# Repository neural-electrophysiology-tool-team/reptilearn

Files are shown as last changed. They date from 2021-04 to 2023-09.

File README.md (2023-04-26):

# Reptilearn

__ReptiLearn__ is an open-source software system for building automated behavioral arenas, running closed-loop experiments based on realtime video analysis, and collecting  behavioral data. 

__ReptiLearn__ was created to help us run continuous, long-term, learning experiments tailored to the specific needs and challenges posed by reptile model animals. 

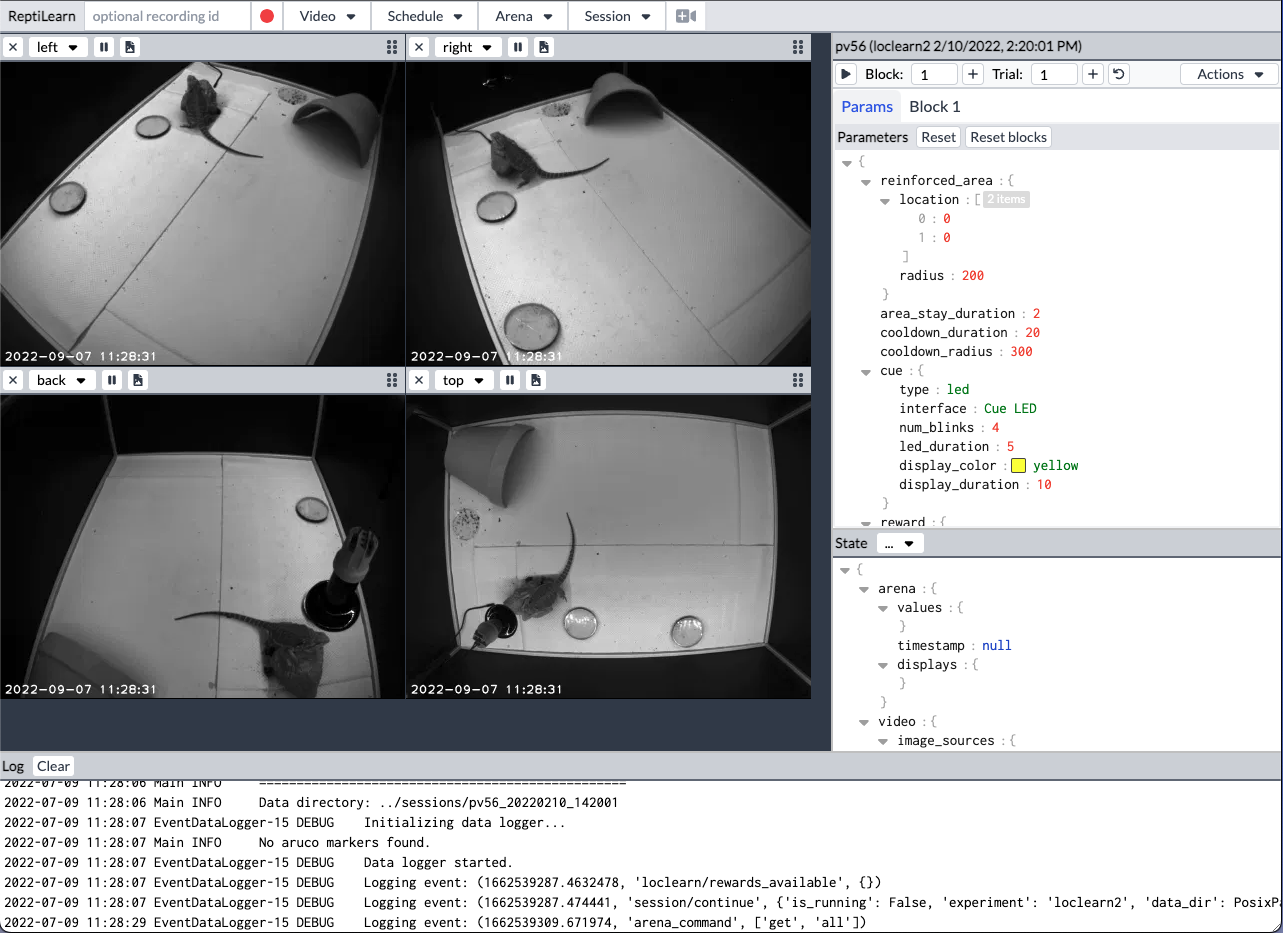
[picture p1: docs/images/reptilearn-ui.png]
ReptiLearn user interface


## Main Features

- Synchronized video recording and real-time analysis from multiple video sources
- Control of various arena hardware such as temperature sensors, lighting, and reward feeders
- Automate and run closed-loop behavioral experiments
- Web based interface for remote monitoring and control
- Highly extendable. Written purely in Python.

## Documentation

- [Getting started](docs/getting_started.md)
- [Building an arena](docs/build_arena.md)
- [Camera configuration](docs/camera_config.md)
- [Setting up the arena controller](docs/arena_setup.md)
- [Programming experiments](docs/programming_experiments.md)
- [Extending the video system](docs/programming_video_system.md)
- [Scheduling tasks](docs/adding_tasks.md)

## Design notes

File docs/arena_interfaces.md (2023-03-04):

# Interface documentation

This document describes the available arena controller interface types and their configuration parameters. 
See [Setting up the arena controller](arena_setup.md) for more information.

## Common interface attributes

- name: Interface name for identification. NOTE: Interface names should be unique across all connected boards.
- type: The interface type. Currently one of `line trigger feeder dallas_temperature`. Each one is explained below.
- ui: Determines how this interface is controlled in the ReptiLearn user interface.

## Interface types and attributes
There are a number of supported interfaces. The `"type"` attribute determines which one is used.

### `line`
Control a single digital output pin. Useful for turning things on and off.

Attributes:
- `pin`: Integer. The Arduino digital pin number to use.
- `reverse`: true | false. Reverse the line output. Will output HIGH when its  state is 0 and LOW when it is 1. 

Commands:
- `get`: Sends back the current state of the line - 0 or 1.
- `toggle`: Set the line state to the opposite of the current one.
- `set <x>`: Set the line state to <x> (0 or 1)
- `periodic <0|1> <period_dur>`: Control toggling the line on and off at a fixed rate. For example `periodic 1 500` will start toggling every 500 ms. `periodic 0` will stop the toggling. The period can be reliably timed at quite short durations. This is useful for blinking LEDs, etc.

Example:
```json
{
    "name": "LED",
    "type": "line",
    "pin": 12,
    "ui": "toggle"
},
```

### `trigger`
Output pulses at a fixed frequency on a single pin. This is used for synchronizing frame acquistion of multiple cameras.

Attributes:
- `pin`: Integer. The Arduino digital pin number to use.
- `pulse_len`: Integer. Time duration in milliseconds between successive pulses. For example, to acquire frames at 20 frames per second this attribute should be 50.
- `pulse_width`: Float. A number between 0 and 1. The pulse duty cycle. The fraction of the pulse period in which the output will be on. For example, a value of 0.8 with a pulse_len of 50ms will result in the digital pin going HIGH for 40ms and then LOW for 10ms before going HIGH again.

Commands:
Like the `line` interface, the `trigger` interface inherits from the toggle interface and has the same commands (`get`, `set`, `toggle`, `periodic`). See the line interface documentation.

Example:
```json
{
    "name": "Camera Trigger",
    "type": "trigger",
    "pin": 12,
    "pulse_len": 17,
    "pulse_width": 0.7,
    "ui": "camera_trigger"
}
```

### `feeder`
Control an EVNICE EV200GW fish feeder (or similar)

Attributes:
- `pins`: Array of 4 integers. The numbers of the pins that are connected to the ULN2003 board.

Commands:
- `dispense`: Dispense one reward from the feeder.

Example:
```json
{
    "name": "Right Feeder",
    "type": "feeder",
    "pins": [5, 6, 7, 8],
    "ui": "action",
    "command": "dispense",
    "icon": "gift"
}
```

### `dallas_temperature`
Communicate with digital temperature sensors such as DS18B20 (one-wire protocol). This uses the DallasTemperature arduino library. Check the [library documentation](https://github.com/milesburton/Arduino-Temperature-Control-Library) for supported devices. This interface can control any number of such sensors connected in parallel over a single Arduino digital pin.

Attributes:
- `pin`: Integer. The one-wire digital pin number. 

Commands:
- `get`: Sends back an array of floats containing the current measurement of each sensor.

Example:
```json
{
    "name": "Temp",
    "type": "dallas_temperature",
    "pin": 2,
    "ui": "sensor",
    "unit": "°",
    "icon": "thermometer-half"
}
```

## Interface UIs
The `ui` attribute determines how the interface is presented in the Arena menu of the ReptiLearn UI. Each `ui` type can have additional interface attributes that configure how it will be displayed in the menu.

### `toggle`

A toggle button that allows setting the interface on or off. It has no additional attributes.

Compatible interfaces: `line`

### `trigger`
This `ui` value tells ReptiLearn to use this interface as a camera trigger. The trigger can be controlled from the trigger button next to the recording button in the UI, or automatically when starting and stopping video recording (in case the trigger was not already running before recording). There are no additional attributes.

Only one interface with the `trigger` ui is supported. Additional interfaces will be ignored by the recording system.

Compatible interfaces: `trigger`

### `action`

A button that sends a command without arguments to the interface. This can be any command.

Attributes:
- `command`: String. The command name. For example, for controlling a `feeder` interface manually it should be set to `dispense`.
- `icon`: String. A name of a FontAwesome icon that will be displayed on the button. See [here](https://fontawesome.com/search?o=r&m=free) for available icons.

Compatible interfaces: any interface that has commands without arguments (e.g. `feeder`)

### `sensor`

Displays the sensor reading, possibly listing multiple sensors that send on the same interface (as in the `dallas_temperature` interface).

Attributes:
- `unit`: String. The units of the sensor value.
- `icon`: String. A name of a FontAwesome icon that will be displayed on the button. See [here](https://fontawesome.com/search?o=r&m=free) for available icons.

Compatible interfaces: `dallas temperature` (but can be used to display the value of any interface).

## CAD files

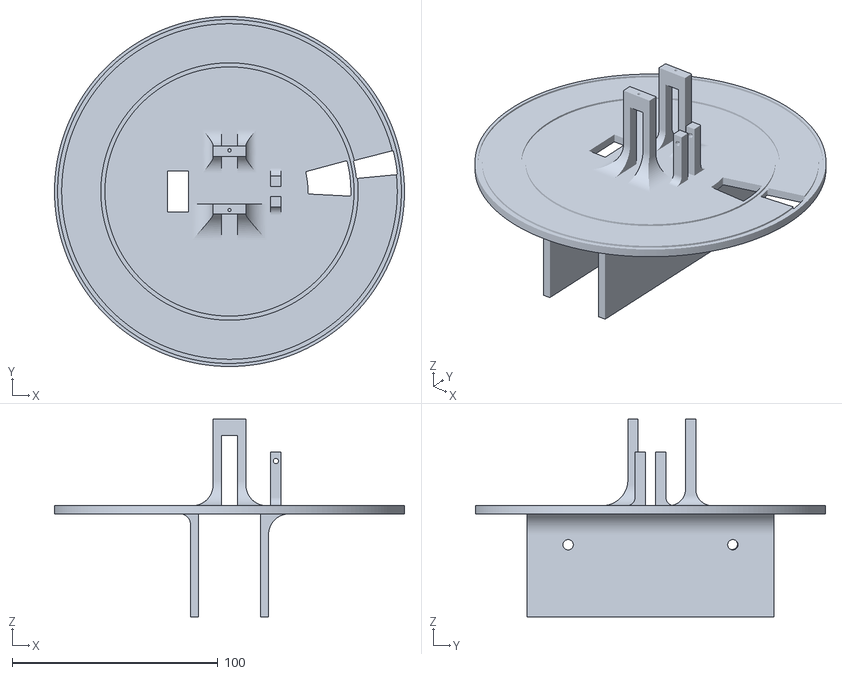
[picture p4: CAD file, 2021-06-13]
autofeeder_project/Base.stl
170.0 x 170.0 x 96.0

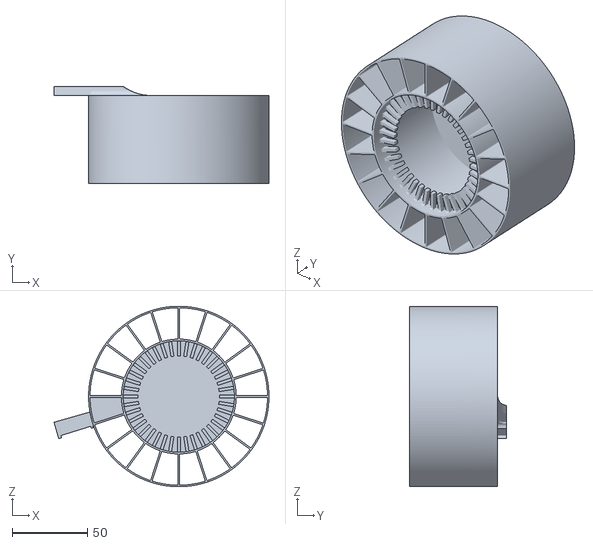
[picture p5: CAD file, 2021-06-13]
autofeeder_project/first_cyn.stl
143.0 x 64.7 x 120.0

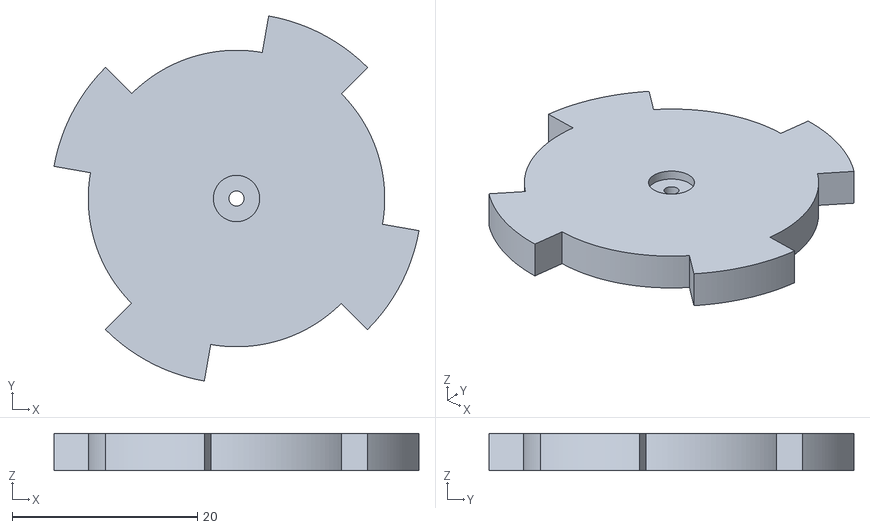
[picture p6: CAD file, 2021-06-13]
autofeeder_project/myGear.stl
39.4 x 39.4 x 4.00

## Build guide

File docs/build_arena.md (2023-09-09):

# How to build a ReptiLearn Arena

This document describes how we built our automated arenas for studying various reptiles. We take no responsibility for any damage caused as a result of following this guide.

## Arena

First build the Arena container.

1. Obtain and cut the wall sheets and frame as necessary (explained elsewhere).
2. Stick anti-reflection wallpapers on the walls. We used black self-adhesive wallpaper rolls suitable to be used as a chalkboard. 
3. Build a box. We used aluminum profiles for the frame and Alucobond sheets for the walls and floor. The floor size was 100x70 cm, and the walls height was 45cm. 
4. To support the top-view camera and other devices (e.g. heat lamps), add another profile one meter above the floor, spanning along the long axis of the box. The profile can be supported by two more profiles connected to the short sides of the box.
5. Connect adjustable camera arms to the top frame of the box, and optionally an additional one on the profile you added on the previous step. We used [this product](https://www.noga.com/Products/modu/Modular%20Holders/LC6100/LC_Arms_-_LC6100). To connect the cameras we used a 3d-printed camera holder that connects the arms to the cameras with screws (STL file TBD).

## Electronics

`General soldering advice: Prevent short-circuits! Use heat shrink tubes for insulation and don't leave any uncovered wires.`

* Decide where and how to place your electronics. This determines the length of the cables you will need to make. Some box or a plate to hold the components could be useful.
* Electronic devices are controlled using Arduino boards. We use “Arduino Nano Every” boards. They are quite inexpensive, have a large enough memory to fit our program, and can be easily mounted on a prototyping breadboard. Other Arduino boards could be used as well but might have a different pinout and/or memory size. Some Arduino boards use 3V instead of 5V. _We didn’t test 3V boards, and some of the components described below might not work in 3V._

### Part 1: Synchronized Camera Trigger (Arduino 1 / 2)

When recording from multiple cameras it’s often desirable that all cameras expose their sensors and take images at the same time. There are several schemes for doing that. We use a single source to trigger all the cameras. One Arduino board is programmed (see elsewhere) to send TTL pulses on one of its output pins. This pin is connected in parallel to the GPIO input of each camera. A two strand cable should go from the Arduino output pin and ground pin (gnd) to the camera GPIO input and ground. Consult the camera manual for the specifics of using its GPIO inputs. In the case of **FLIR cameras** we use their GPIO cable that connects to the camera on one side and has colored wires on the other. ReptiLearn sets the cameras to use Line3 by default (but this can be changed). For example, for a Firefly camera, this page: [Input/Output Control FFY-U3-16S2](http://softwareservices.flir.com/FFY-U3-16S2/latest/40-Installation/InputOutputControl.htm) will tell you to connect the Arduino output to the green wire and the ground pin to the brown wire.

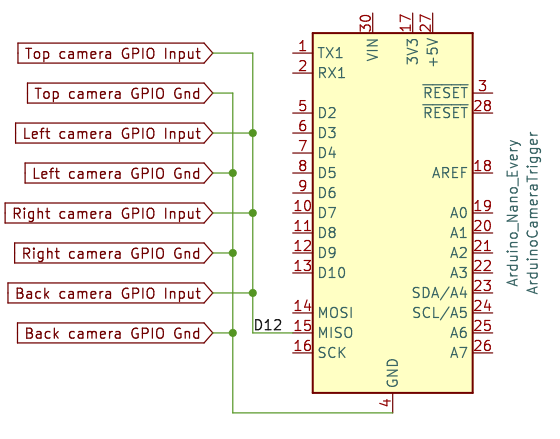
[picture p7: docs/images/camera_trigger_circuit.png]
Camera trigger circuit diagram


Connection diagram showing how to connect four cameras to an Arduino Nano Every board. To find the location of each I/O connection on the board check this page (for this specific board): [Nano Every | Arduino Documentation](https://docs.arduino.cc/hardware/nano-every). Look for the pinout.

```
Note: Don't use the camera trigger Arduino board for anything other than sending triggers. Communication with other components might cause the trigger timing to vary.
```

### Part 2: The Feeder (Arduino 2 / 2)

To reward the animals we used a Fish Feeder (EVNICE EV200GW). This feeder normally has a latency of about 15 seconds which might not be acceptable for some tasks. We reduced the latency to about 3 seconds by interfacing directly with the feeder motor. 

The feeder has a 28BYJ-48 stepper motor. We control it by connecting it to a ULN2003 stepper motor driver board that looks like this:

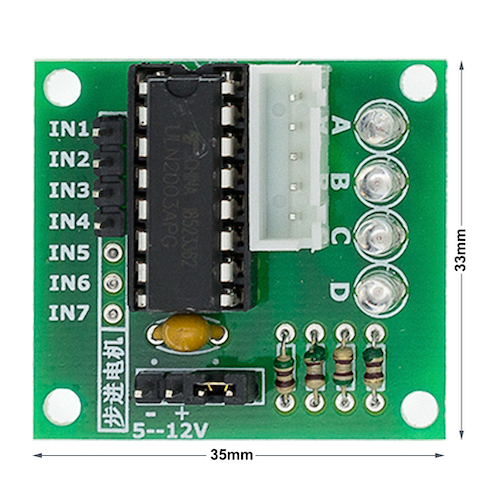
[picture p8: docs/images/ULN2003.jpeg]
ULN2003 Board


The layout of this specific board is easy to work with as you’ll see. As mentioned, you shouldn’t connect this to the camera trigger Arduino. Use a second one and follow these steps:

1. Unscrew and remove the bottom plastic cover of the feeder
2. Remove the plastic cover that hides the motor
3. Disconnect the motor cable from the feeder board and connect it to the white header on the ULN2003 board.
4. The feeder has a DC power socket. This socket is connected to the board with a small cable with 2 wires. Disconnect it from the board and connect it to the power inputs on the ULN2003 board (usually marked + -, black header on the right side in the picture above). The red power wire goes to the +, the black goes to the minus (ground). To make this connection we use male to female dupont jumper wires. The male pins can be inserted into the correct pins of the 3-pin socket, and the female pins connect to the ULN2003 board. Alternatively you can cut off the 3-pin socket and solder dupont female pins directly to the black and red wires. Technically the ground should also be connected to the Arduino GND pin but we found this to be usually unnecessary. This is the first thing to check if something doesn’t work, though.
5. Connect the four inputs marked IN1-IN4 to digital pins on the Arduino board (e.g. D9, D10, D11, D12).
6. Close and screw the bottom cover back, making sure all the wires can get to where they need to be. There are 4 LEDs on the board that light up in sequence during feeding, you might want to hide or show these depending on your needs.
7. Use the mounting mechanism provided together with the feeder to fix everything to the top frame of the arena.
8. Connect a 5V DC power supply to the DC power socket on the feeder. A maximum current of about 500mA should be enough.

Our setup is very similar to the one described [here](https://lastminuteengineers.com/28byj48-stepper-motor-arduino-tutorial/)

### Part 3: Temperature sensors

We use two digital DS18B20 temperature sensors for measuring temperature conditions in the arena. These can come in a metal or plastic packaging and have 3 wires. They use the [1-Wire](https://en.wikipedia.org/wiki/1-Wire) protocol to communicate with the Arduino, enabling up to 128 sensors to be connected in parallel using a single Arduino digital pin.

See [here](https://lastminuteengineers.com/multiple-ds18b20-arduino-tutorial/) for more info.

* The sensor has 3 IO pins: VDD (5v), GND (ground), and DQ. First figure out which wire is which.
* Then, for each sensor, use a cable with 3 or more wires, and connect VDD to the +5V pin of the Arduino board, GND to the GND pin, and DQ to a digital I/O pin. 
* Additionally, VDD and DQ must be connected with a 4.7kOhm pull-up resistor. The resistor can be shared between all sensors (each DQ to one side of the resistor and each VDD to the other).

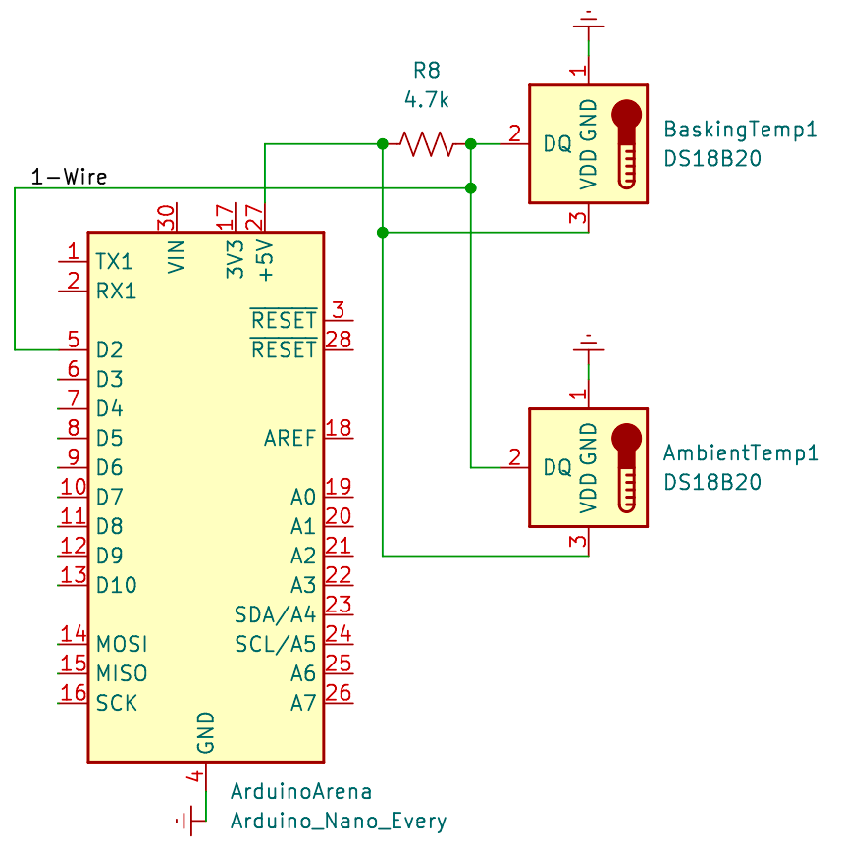
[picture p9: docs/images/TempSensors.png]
Temperature Sensors circuit diagram


### Part 4: Controlling things with relays

A relay is a mechanical device that can close or open a circuit based on a control voltage. Any device that requires a high current, which you want to switch on and off requires a relay. We used relays for controlling an LED strip that lights the arena, as well as heat lamps.

We used [this](https://www.pololu.com/product/2480/) board which includes an Omron G5LE-14-DC5 SPDT relay.

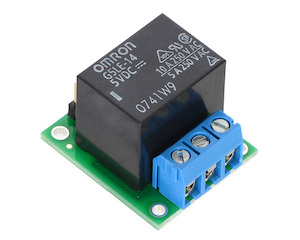
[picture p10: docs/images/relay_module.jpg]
Relay module


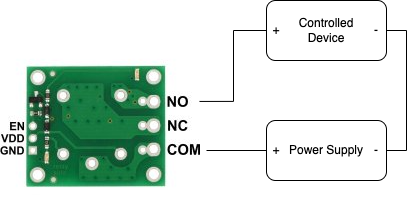
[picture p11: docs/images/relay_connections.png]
Example relay circuit diagram


The relay board has 6 I/O connections. EN, VDD, and GND connect to the Arduino board (male pins in front of the image above), and NO, NC, and COM are the controlled connections (blue socket with screws in the back of the image above). Connect VDD to the Arduino +5V pin, and GND to the Arduino GND (ground) pin. EN, the signal pin, should be connected to one of the Arduino’s digital output pins. 

The relay has two modes of operation depending on which connections are used for connecting the controlled device. The NO (Normally open) pin is connected to the COM (common) pin only when the EN pin is high (i.e., when there’s a 5v voltage between EN and GND). The NC (Normally closed) pin is connected to the COM pin only when the EN pin is low (no voltage across EN and GND). We always use the NO pin so that current will only arrive to the device when the Arduino is running and its digital pin is high.

In practical terms one of the wires going from the power supply to the controlled device (positive in the diagram above) should be cut somewhere in the middle, and then the half that goes from the power supply should be connected to COM, and the other half to NO (see diagram above).

We connected both a LED strip and heat lamps using this method. The relay can be connected to either the AC or DC part of a DC power supply. You may want to connect multiple devices to the same power supply in parallel (e.g. multiple heat lamps to the same power supply). In this case you would want to connect the relay to each cable that connects the power supply to one of the devices in order to be able to control each device individually.

### LED Strip

We used a 12V cold-white LED strip to light the arena. The LED strip is taped to the top frame and covers the four top edges of the arena. This results in a mostly uniform light level across the arena floor, and helps to minimize shadows. The total length is then around 3.4 meters, which required a 12V 5A DC power supply for the strips we used (consult your LED strip manufacturer for the maximum current it might draw, and adjust the power supply as necessary).

### Heat Lamps

We had success using these [IR halogen heat lamps](https://he.aliexpress.com/item/4001212438174.html?spm=a2g0o.productlist.0.0.3b561783JmP4VQ&algo_pvid=f1c2b25b-032a-41a0-b267-9318c73811c5&algo_exp_id=f1c2b25b-032a-41a0-b267-9318c73811c5-25&pdp_ext_f=%7B%22sku_id%22%3A%2210000015319775871%22%7D&gatewayAdapt=glo2isr).

They are 24V 50W DC lamps which means that they will need a current of at least 50/24=~2A per lamp, however halogen lamps can have a much lower resistance when they are cold and therefore can take much more current initially. It is recommended to use a power supply with at least double the current (e.g. 4A per lamp or more). We used a 24V 12A DC power supply for two lamps.

## Touch screen

A touch screen can be connected to the arena computer in the usual way. ReptiLearn has support for switching the screen on or off (linux only, currently). 

We used a Dell monitor with good results for behavioral experiments. For using a touch screen while making electrophysiological recordings, we used [this monitor](https://www.connection.com/product/elo-touch-solutions-accutouch-1790l-17-lcd-open-frame-touchscreen-display-hdmi-vga-displayport-usb/e326347/34520493?cac=Result) to reduce electromagnetic noise.

We mount the monitor using screws to one of the shorter (0.7m) sides of the arena. A Kappa board or some other strong board can be used to hide the monitor cables and prevent the animal from using the monitor to escape. Cut it to fit into the arena, and make a square hole that fits the monitor (that is, make a frame for the monitor).

## Finishing touches

Once everything is built, follow these final steps:

* Mount the cameras using the camera holders
* Connect Cameras and Arduino boards to the computer using USB cables. Make sure the camera cables support a fast enough USB mode to reach the frame rates you want to record in. We had success with the [FLIR USB cables](https://www.flir.eu/products/usb-3.1-locking-cable/) that are sold on their website.
* Connect GPIO cables to cameras
* Place Arduino boards and other electronic components in their final location (e.g. a box or plate)
* Hide cables and make it look tidy and neat.
* Connect power supplies
* [Setup the ReptiLearn software](getting_started.md)
* Have fun

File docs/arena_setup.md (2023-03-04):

# Setting up the arena controller

ReptiLearn can control and monitor various electronic devices by communicating with [Arduino boards](https://www.arduino.cc/). Some examples include lights, cue LEDs, temperature sensors, reward feeders, and camera triggers. 

You can connect any number of devices to one or multiple Arduino boards, and control all of them without having to write any Arduino code. This is accomplished by using a single Arduino program that can interface with a number of different types of components. Each Arduino board is automatically programmed with the same generic program, and once communication between the board and computer software is established, each board is configured based on its individual settings.

## The arena controller

Communication with, and programming of the boards is handled by the Arena controller ([arena.py](../arena/arena.py)). The ReptiLearn software communicates with the controller using the [MQTT](https://mqtt.org/) protocol. The controller provides bi-directional communication between MQTT clients and connected Arduino boards.

By default, ReptiLearn will start the arena controller as a sub-process when it starts up, unless the arena config file is empty. It's also possible to run the controller separately, or even on a different computer. See [here](#run-arena-controller-separately) for more information. In the rest of the document it's assumed you're running the controller as a sub-process.

## Supported Arduino boards

The arena controller should work with any Arduino board that has at least 48KB of program memory and 4KB of RAM. Check your model specifications. At the time of writing, most available boards do not have enough memory. We used Arduino Nano Every boards which work well and are relatively low cost.

## Configuring the arena controller

The arena config file is stored by default in `reptilearn/system/config/arena_config.json`. To make changes you can use the arena settings dialog:

- Run ReptiLearn
- Open the ReptiLearn web app in a browser
- Open the Arena menu by clicking the button
- Click on "Arena settings" to open the settings dialog

### Adding Arduino boards

- Connect an Arduino board
- In the settings dialog, click the plus (+) button
- You should be able to select the port of the board in the dialog that opens.
- Choose a name for this Arduino, and fill in the FQBN of your board (see below).
- Click the add button
- The new board configuration should appear. 
- Click on the save button to save the new config file.

### Fully qualified board name (FQBN)

The FQBN string identifies the Arduino board type, and is necessary for uploading programs to the Arduino. To find the FQBN of your board run:

```bash
arduino-cli board listall
```

For example for __Arduio Nano Every__ the FQBN is `arduino:megaavr:nona4809`.

### Uploading the program

After you saved the arena configuration you can upload the program to the Arduino board you added:

- Open the "Arena settings" again
- Choose the new board from the board list (according to the name you chose when you added it)
- Click on "Upload program"

The upload process should begin and you should see messages in the log.

### Not enough memory error
As mentioned above, many Arduino boards do not have enough memory to store the arena program and run it. If you use one of these boards you will encounter a "not enough memory" error while trying to upload.

In most cases getting a supported board model should solve this problem, however it's also possible to reduce the storage space requirements of the program by removing unnecessary interface types from the source code. To do that, open [arena/arduino_arena/arduino_arena.ino](../arena/arduino_arena/arduino_arena.ino), and comment out any of the lines that start with `#include` for interfaces that you don't need. See the comment in the includes section of the .ino file.

### Connecting multiple boards

You can repeat the previous steps with any number of additional Arduino boards. It is recommended to connect the boards one-by-one, to make them easier to identify.

### Adding interfaces

After adding an arduino board you need to configure its interfaces. These define which devices are connected to the board and their parameters, including how they will appear in the Arena menu. 

You can configure interfaces in the "Arena settings" dialog. After choosing the Arduino board you want to configure, the interfaces array should show up in the configuration editor. As a simple example, edit your config to look like this:

```json
{
    "serial_number": "<board serial>",
    "fqbn": "<board fqbn>",
    "interfaces": [
        {
            "name": "LED",
            "pin": 13,
            "type": "line",
            "ui": "toggle"
        }
    ]
}
```

Then click the save button, and if the arena controller wasn't already running, open the Arena menu and click "Start arena".

Assuming all went well, the controller should now run and the new interface should appear in the Arena menu. Clicking on the interface button (labeled LED with a toggle icon) should turn on the LED.

See [here](arena_interfaces.md) For more information about interfaces.

NOTE: Some boards have a built-in LED connected to pin 13. If that's not the case for your board, you can connect one between pin 13 and the ground pin of the board (if needed use an appropriate resistor in serial with the LED). 

### Allow get

The system periodically polls each board for its current state (every minute by default). It also requests the value of each interface after sending it a command. This might take some time and prevent the board from doing other things, therefore it should be avoided for time-sensitive functions (such as the camera trigger).

The `allow_get` board parameter can be set to `false` in the arena config in order to prevent sending these state updates. 

## Arena menu

The Arena menu in the web app lets you manually send commands and monitor sensors, as well as stop and re/start the arena controller. Each interface is displayed in the menu according to its configuration. The "Poll arena" button will request each board for its current state and update the menu and system state accordingly.

## Run the arena controller separately

The arena controller can be run as a separate program instead of as a sub-process of the main system. This allows running the controller on a different computer. In this case it's not possible to program the boards or start and stop the controller from the ReptiLearn web app.

To run the controller on another computer, download and install reptilearn as described [here](getting_started.md#installation) on both computers. Make sure to install [Arduino-CLI](getting_started.md#arduino-cli-optional) on the computer that will run the arena controller.

To prevent ReptiLearn from running the controller on startup open your config file and set the `run_controller` attribute in the arena dictionary to False. For example:

```python
arena = {
    "run_controller": False,
}
```

Restart ReptiLearn if it's already running for the change to have effect.

### Configuration

Here we assume you are running the controller from the same ReptiLearn installation as the ReptiLearn system. See more information [below](#running-remotely) if you want to  run it remotely.

#### Adding boards

When running the controller separately it's not possible to find available boards in the "Add Arduino" dialog, as before. To find the serial number of your arduino, open a terminal pointing to the reptilearn directory (use Anaconda prompt on windows), and run the controller with the `--list-ports` argument:

```bash
cd arena
conda activate reptilearn
python arena.py --list-ports
```

You should see a list of all available serial ports with their serial numbers. Find the FQBN of your board with `arduino-cli` as explained [above](#fully-qualified-board-name-fqbn).

### Uploading the program

After configuring the boards in "Arena settings", use the controller again to upload the program. Upload to all configured boards by running:

```bash
cd arena
conda activate reptilearn
python arena.py --upload
```

To upload to a specific board run:

```bash
python arena.py --upload <board_name>
```

Where <board_name> is the name that was chosen when configuring the board.

### Running the controller

To run the controller open a terminal (Anaconda prompt in Windows) window pointing to the reptilearn directory, and run:

```bash
cd arena
conda activate reptilearn
python arena.py
```

OR if you want to use a different config module than the default (the default is at arena/config.py):

```bash
conda activate reptilearn
cd arena
python arena.py --config config-module
```

where `config-module` is the name of a python module containing the config values without the .py extension.

Once the board is running, log messages should appear in the ReptiLearn web app, and the Arena menu should show the configured interfaces.

Press Ctrl-C to stop the controller.

### Running remotely

When running the controller on a different computer its necessary to set the same MQTT broker host and port, in both the ReptiLearn config file, and the controller config file at [arena/config.py](arena/config.py). See [here](getting_started.md#remote-mqtt-broker) for more information on using a remote MQTT broker.

Both installations should also have a copy of your `arena_config.json` file. This is the file that is edited using the "Arena settings" dialog. You can usually find it at `system/config/arena_config.json`, but you can change its location by editing `arena_config_path` in both config files.

After doing the previous steps, you can run both ReptiLearn and the arena controller as described above. They should be able to communicate with each other through the MQTT broker.

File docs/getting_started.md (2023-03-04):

# Getting started

## Installation

The software was mostly tested on Ubuntu 20.04, but also works on MacOS, Windows, and probably other linux distributions (although some features might not work).

Follow these steps to install:

### Download

- Install [Git](https://git-scm.com/downloads)

- Open a terminal (git bash on windows), change the directory to where you want to install, and run:
 
 ```bash
 git clone https://github.com/neural-electrophysiology-tool-team/reptilearn
 ```

### Setup Python environment

- Install [Anaconda](https://www.anaconda.com/)

- Run the following from the same directory to create a reptilearn Python environment (on Windows use Anaconda Prompt):

```bash
cd reptilearn
conda env create -f environment.yaml
```

This should install all the necessary Python dependencies.

### Build the UI webapp

- Install [Node.js](https://nodejs.org/en/)

- Run the following in a terminal window pointing to the `reptilearn` directory to install node.js dependencies and build the webapp:

```bash
cd ui
npm install
npm run build
cd ..
```

### MQTT broker (optional)

Communication with Arena hardware and other software components (e.g. touchscreen apps) is done using the [MQTT](https://mqtt.org/) protocol. When starting up ReptiLearn it tries to connect to an MQTT broker running on the same machine on the default MQTT port (1883). If a connection was not successful you will see an error message, but other parts of the system can still be used.

We recommend installing [Eclipse Mosquitto](https://mosquitto.org/). To use a broker running on a different machine see [Remote MQTT broker](#remote-mqtt-broker) below for more information.

NOTE: ReptiLearn doesn't currently support non-anonymous access to the MQTT broker. If you're using Eclipse Mosquitto and have problem connecting (connection refused), add the following line to your mosquitto.conf file:

```
allow_anonymous true
```

### Arduino-CLI (optional)

For programming Arduino boards you need to install [arduino-cli](https://arduino.github.io/arduino-cli/latest/installation/).

Once installed, run these commands to install the necessary Arduino libraries:
```
arduino-cli core update-index
arduino-cli lib install AccelStepper ArduinoJson OneWire DallasTemperature
```

Finally, install the software for your specific Arduino board model(s). For example for an Arduino Nano Every or UNO WiFi Rev 2 run:
```
arduino-cli core install arduino:megaavr
```

For other models, the following command will list all available board IDs:
```
arduino-cli core list --all 
```

When you have your board ID, install the core for it using this command:
```
arduino-cli core install <board ID>
```

Repeat this for each type of board you intend to use.

### FFmpeg setup (optional)

[FFmpeg](https://ffmpeg.org/) is used to encode video files. Normally it should be installed together with the ImageIO library when creating the anaconda environment, however if you want to use a different installed version (for example one that supports encoding on a GPU), create the file `reptilearn/system/.env` with the following content:

```
IMAGEIO_FFMPEG_EXE=/path/to/ffmpeg/executable
```

## Configuration

The system uses python modules as configuration files. The default configuration can be found at [system/config/config.py](/system/config/config.py). You would probably want to make some changes before running for the first time. It's possible to make changes directly in the default config file, but we recommend creating a new config file (e.g. system/config/my_config.py). 

Any values not defined in the new config file will be taken from the default config file. To use the new config, run with a `--config my_config` command line argument (see [Running](#running) below).

For example, this is how a config file that only changes the web server port value would look like:
```python
web_ui = {
    "port": 3501,
}
```

You probably want to change the directories for storing data:

- `session_data_root`: This is where session data will be stored (each session is stored in its own subdirectory)
- `media_dir`: Videos and images are stored here when there's no open session

Make sure these directories exist before running.

## Running

- If you're using a local MQTT broker, make sure it's running
- In a terminal (Anaconda Prompt on Windows) switch to the installation directory and run:

```
cd system
conda activate reptilearn
python main.py
```

OR if you want to use a different config module:

```
cd system
conda activate reptilearn
python main.py --config my_config
```

where `my_config` is the name of a python module inside the `config` directory without the .py extension.
For example, ```python main.py --config config2``` will start the system configured according to `system/config/config2.py`.

- Open a recent version of your favorite web browser, and go to [`http://localhost:3500`](http://localhost:3500). You can access the web app remotely by using an ssh tunnel or by using the computer's IP address instead of `localhost`.

NOTE: We recommend using ssh tunnels and/or a VPN to securely access the web app. ReptiLearn has no support for user authentication or any other security measures.

## Database

A [TimescaleDB](https://www.timescale.com/) database can optionally be used to store log data. To use this feature, you first need to install the database (see the link above for information). [Docker image installation](https://docs.timescale.com/install/latest/installation-docker/) is recommended. 

If you use the Docker image, you must also install [`psql`](https://www.timescale.com/blog/how-to-install-psql-on-mac-ubuntu-debian-windows/) separately.

Once `psql` is installed, install the [psycopg2](https://pypi.org/project/psycopg2/) library into the anaconda environment you created previously:

```bash
conda activate reptilearn
pip install psycopg2
```

Lastly, you need to create a new database. This can be done by running the SQL command (this can be done using [psql](https://www.postgresql.org/docs/current/app-psql.html)): 
```sql 
CREATE DATABASE reptilearn;
```

## Real-time object detection using YOLOv4

ReptiLearn currently supports real-time object detection using the YOLOv4 neural network model. YOLO can be used to obtain bounding boxes of relevant objects in image streams (such as your subject animals). We use the original darknet version from [this](https://github.com/AlexeyAB/darknet) repository. Darknet requires a CUDA capable GPU, and working installations of NVIDIA CUDA, and cuDNN.

First, configure your cameras or other image sources (see [Camera configuration](docs/camera_config.md) for more information), then follow these steps to setup the model:

- [Compile darknet](https://github.com/AlexeyAB/darknet#how-to-compile-on-linux-using-make). We recommend using the `make` method. Make sure to set `LIBSO=1` in the `Makefile` to compile into a static library.

- Copy the compiled library `libdarknet.so` from the YOLOv4 directory into `reptilearn/system/image_observers/YOLOv4`

- Generate/copy model weights and configuration: To train the model to detect your custom objects follow this [section](https://github.com/AlexeyAB/darknet#how-to-train-to-detect-your-custom-objects) in the darknet documentation. Another option is to use pre-trained weights. In either case you should end up with three files: A `.cfg` file containing your network configuration, an `obj.names` file containing a list of object classes, and a `.weight` file containing the trained model weights. Copy these files into `reptilearn/system/image_observers/YOLOv4`.

- Add the YOLOv4 image observer: In the ReptiLearn web app, open the `Video` menu and click on `Video settings`. Switch to the `Observers` tab, and click the + (plus) button. Choose the class `yolo_bbox_detector.YOLOv4ImageObserver` and enter a descriptive id. A new image observer should be added, and its default parameters should be displayed in the settings window. 

- Configure the image observer. Assuming you copied the model files according to the step above, edit the following observer parameters:
    - `cfg_path`: set to `image_observers/YOLOv4/<your .cfg file name>`
    - `weights_path`: set to `image_observers/YOLOv4/<your .weight file name>`
    - `src_id`: The id of the image source you want this observer to analyze 
    - Additional parameters you may want to change are:
        - conf_thres: Detections with lower confidence than this value will be ignored
        - nms_thres: Threshold for the non-max suppression algorithm. 

- Click the `Apply & Restart` button to restart the video system and load the new observer.

Assuming everything worked, the YOLOv4 model should now be loaded and you should see a log message in the web app. If you don't see any message, check the terminal window where ReptiLearn is running for any errors coming from the YOLO model. 

NOTE: To use the detection data in real-time or store it you need to run the appropriate experiment. See [Programming experiments](docs/programming_experiments.md) for information about interfacing with image observers.

see [Extending the video system](docs/programming_video_system.md) for information about adding support for additional models.

## Remote MQTT broker

ReptiLearn can be configured to use a remote MQTT broker. To do so, edit your config file and change the `host` value of the `mqtt` dictionary. You may also need to change the `port` value if the remote broker uses a different port.

```python
# MQTT server address
mqtt = {
    "host": "<remote MQTT broker host name>",
    "port": <remote broker port number>,
}
```

You will also need to change these values in the arena controller configuration file at `reptilearn/arena/config.py`:

```python
# MQTT settings
mqtt = {
    # Server host and port number
    "host": "<remote MQTT broker host name>",
    "port": <remote broker port number>,

    ...
}
```

After restarting ReptiLearn it should use the new broker configuration.

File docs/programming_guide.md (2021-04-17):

# Experiment Programming Guide

## Starting the system

To start the system change to the `./system` directory and run `python main.py`. The system configuration is stored in a python module inside the system/config directory. The --config argument can be used to specify a custom config module, otherwise, the config/config.py module is used by default.

## Creating a new experiment module

To create a new experiment type create a new python module file and save it in the experiments modules directory (as specified by the `experiment_modules_dir` attribute in the configuration file, `<reptilearn root>/system/experiments/` by default). The module should contain a single subclass of the experiment.Experiment class.

## Loading an experiment

Once the file is created, click on the “Refresh list” option under the experiment list dropdown in the web-ui. The experiment name should now appear on the list. Selecting it will set the current experiment to the newly created one.

To update the code of a loaded experiment, save your code changes and click the “Reload” button.

## Experiment lifecycle

An experiment goes through several lifecycle events, each event invokes a method of the experiment class which was defined in the experiment module:

- `setup(self)`: called when the experiment is loaded.
- `run(self, params)`: called when the experiment starts, usually by pressing the “Run” button.
- `end(self, params)`: called when the experiment ends, either by pressing the “End” button, or when all experiment phases have finished (see below)
- `release(self)`: called when the experiment is unloaded (another experiment is loaded, the system shuts down, etc.).

Experiments can have a number of phases - trials and blocks. Blocks can have distinct parameters (see experiment parameters below), and may contain any number of trials sharing the same parameters. The current block and trial are stored in the state path `(“experiment”, “cur_block”)` and `(“experiment”, “cur_trial”)` respectively (see system state below).

When running an experiment, the first block and trial start running (this might change in the future).
The experiment class has the following method hooks for blocks and trials:

- `run_block(self, params)`: called when a block starts.
- `end_block(self, params)`: called when a block ends.
- `run_trial(self, params)`: called when a trial starts.
- `end_trial(self, params)`: called when a trial ends.

When loading an experiment its blocks will show up below the experiment parameters. Blocks can be added, removed, duplicated, or shuffled around, using the buttons in the block section in the web-ui.

Once an experiment is running, it is possible to move to the next block or trial manually by pressing the plus buttons below the experiment bar, or by calling the `experiment.next_block()` and `experiment.next_trial()` functions.

## Experiment parameters

An experiment can have customizable parameters that can be assigned using the web-ui. Any parameter can be added, however usually experiments define default parameter names and values as described below. These will show up in the web-ui after loading the experiment (or after pressing the “Reset” button). In addition, each block can define additional parameters as well as override experiment parameter values.
The parameters are passed as an argument to each lifecycle method. run() and end() receive the experiment parameters as a dictionary, and `run_trial()`, `end_trial(), run_block()`, and `end_trial()` receive the relevant parameters for the current block - the experiment parameters are overridden with values defined in the block parameters.

### Defining default parameters and block parameters

To define default experiment parameters add a dictionary as a `default_params` class attribute to the experiment class. To define default blocks and block parameters add a `default_blocks` list in which each element is a dictionary containing default block parameters. For example:

```python
class MyExperiment(experiment.Experiment):
    default_params = {
            "param1": param1-value,
	            "param2": param2-value,
		            ...
	}

    default_blocks = [
            {"param1": overridden-param1-value, "param3": some-value},
	            {"param2": overridden-param2-value, "param4": some-value},
	]
```

This code will define an experiment with some default parameters, and two default blocks, each overriding one parameter and defining another default block parameter.

### Built-in parameters (could change in the future)

Some parameters have a special meaning for the system:
- num_trials: determines the number of trials for each block. This can be either an experiment parameter or defined individually for each block. When this parameter is defined, once this number of trials are executed the block will end, moving to the next block or ending the experiment if the current block is the last one.

## System state

The system maintains a global synchronized state using the state module. The state is a nested dictionary structure that can be shared between processes (see multiprocessing below), and contain the current state of the system. The state can be accessed using state.Cursor objects, and callback can be added to listen for updates of specific state values. See the documentation of the state module for more information.
The current state of the system is shown in the web-ui in the state section (under the experiment section).

## Data collection and storage

Whenever an experiment is starting, a data directory is created for it under the experiment data root directory (determined by the `exepriment_data_root` config attribute). The directory name is based on the experiment id (which can be set in the web-ui), and it's stored in the state path `("experiment", "data_dir")`.

Once the directory was created, any data will be stored inside it. This could include recorded videos and images, the log file (`experiment.log`), the event log and any other data logs (see below).

### Logging

The experiment class provides a python logger object (self.log). Messages sent to this logger will appear in the web-ui and saved to the experiment log file.

### Data logs

Time series data that's collected during the experiment can be stored to csv files and/or to the database using a data logger. The `data_log.QueuedDataLogger` class, a subclass of `data_log.DataLogger`, provides a simple mechanism for defining data tables, and adding rows of data. See the `data_log.py` documentation for more information.

### Event log

The event log is a special DataLogger that can be used to automatically log an event whenever specific state paths are updated, or when mqtt messages are published on specific topics. It is configured in the `event_log` dictionary of the config module, and default events that should always be recorded are defined there. The event log is created when the experiment starts (before calling its `run` method), and the logger can be accessed through the module attribute `experiment.event_logger`. Once the event log was created, events can be added or removed. Custom events can be logged by calling the `log` method. See the `event_log.py` documentation for more information.

### Video recordings and snapshots

Synchronized video recording from multiple image sources (see below) is handled by the `video_record` module. The recorder can be configured under the `video_record` config attribute. To start and stop recording use the `video_record.start_record` and `stop_record` functions. Image sources can be selected from the web-ui, by explicitly listing them in `start_record` or by using `video_record.set_selected_sources`, `video_record.select_source`, or `video_record.unselect_source`. 
If the cameras are configured to synchornize with a ttl trigger, it can be started and stopped using `video_record.start_trigger`, and `video_record.stop_strigger`, or by clicking the trigger button in the web-ui. When the trigger is already running before starting a recording, it will automatically pause, and start once the recording starts. 

To take a single snapshot of the current image for each selected image source use `video_record.save_image`. A single image for each source will be saved in the experiment data directory.

The current state of the video recorder can be accessed under the `("video_record")` state path.

For more information see the video_record module documentation.

## Controlling the arena 

The arena module provides functions for controlling the arena hardware. It also listens for sensor reading, and stores them, together with the state of the various components under the `"arena"` state path. The arena can also be controlled from the Arena menu in the web-ui top panel. See the arena module documentation for more information.

## MQTT client

Communication with image observers and programs running on the touchscreen is handled through the MQTT protocol. The mqtt module provides a client running on the main process which can be accessed through the `mqtt.client` module attribute. See the mqtt.MQTTClient documentation for more information.

## Scheduling

The schedule module provides a number of functions for running tasks on various time schedules. See the documentation for more information.

## Image Sources and Image Observers

The processing and analysis of image data is done by `ImageSource` and `ImageObserver` classes. ImageSources run as separate processes and acquire a stream of images from some source (such as a camera). The image data is stored in a shared memory that can then be accessed by any number of ImageObservers. ImageSources are defined in the image_sources config module dict. The dict keys are the image source ids, and are used for selecting record sources, and defining ImageObservers.

ImageObservers also run on separate processes. They are attached to specific ImageSources and are notified by the source when new image data is available. Observers can communicate with the experiment (running on the main process) through MQTT (usually when dealing with large amounts of data, such as the bounding box coordinates of the animal for each frame), or by updating the central state. State updates should be regarded as slow, since each update and access effectively make a copy of the entire state.

The observers are defined under the image_observers dict in the config module. The observer instances are stored in a dict that can be accessed through the `experiment.image_observers` module attribute. Both dicts use keys as they are defined in the configuration. The observers and their processes are all created on system startup, however they wait and do nothing until receiving a start message. To start and stop an observer invoke its `start_observing` and `stop_observing` methods respectively.

The video_stream module is responsible for image sources and observers functionality, and the base classes defined there can be subclassed to create new source and observer classes.

## Accessing config attributes

Since the config module is selected dynamically at system startup, it should only be accessed by using the `experiment.config` module attribute. This holds a reference to the config module that is being used.

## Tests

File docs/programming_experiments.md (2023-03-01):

# Programming experiments

Coming soon...

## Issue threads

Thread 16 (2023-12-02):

### ISSUE TITLE
Arduino board ID

### ISSUE THREAD

**Issue by netta-hub** [neural-electrophysiology-tool-team/reptilearn#16]
on the last step of the arduino-cli installation this line is written:

arduino-cli core install <board ID>

how do I get to the board ID?

thnx

**Comment by eisental** [comment]
Running `arduino-cli core list --all` should print all existing IDs (left column). For "Arduino Nano Every" the right ID is arduino:megaavr. For other boards find the ID according to the Name column. By the way, we moved the repository to here: https://github.com/EvolutionaryNeuralCodingLab/reptiLearn. Any updates will be done there from now on.

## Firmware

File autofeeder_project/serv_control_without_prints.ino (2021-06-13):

#include <Servo.h> 

Servo myservo;

#define SensorPin A0
#define MasterPin 3
#define ServoPin 9

String cmd;
String instring;
int inint;
int sensorvalue=0;
int pr=0;
int threshold=30;

int start_spin = 0;
int wait_to_end = 1;
int wait_for_cmd = 2;
int flag=0;
int counter_flag=0;
int prev_read = 0;
int feeding_cells=0;

String getValue(String data, char separator, int index)
{
    int found = 0;
    int strIndex[] = { 0, -1 };
    int maxIndex = data.length() - 1;

    for (int i = 0; i <= maxIndex && found <= index; i++) {
        if (data.charAt(i) == separator || i == maxIndex) {
            found++;
            strIndex[0] = strIndex[1] + 1;
            strIndex[1] = (i == maxIndex) ? i+1 : i;
        }
    }
    return found > index ? data.substring(strIndex[0], strIndex[1]) : "";
}



void setup() {
  Serial.begin(9600); // debuggig, instead of master interrupt

  myservo.attach(ServoPin);
  myservo.write(90); //set the servo to no movement
  
  //pinMode(SensorPin, INPUT_PULLUP);
  //pinMode(MasterPin, INPUT_PULLUP);
  //attachInterrupt(digitalPinToInterrupt(MasterPin),start_servo,RISING);
  //attachInterrupt(digitalPinToInterrupt(SensorPin),stop_servo,RISING);
}

void loop() {
  sensorvalue=analogRead(SensorPin);
  if(Serial.available())
  {
    cmd = Serial.readStringUntil('\n');
    if (cmd.startsWith("spin"))
    {
      instring = getValue(cmd, ' ', 1);
      inint=instring.toInt();
      myservo.write(inint);
    }
    else if (cmd.equals("stop"))
    {
      stop_servo();
    }
    else if (cmd.startsWith("sens"))
    {
      instring = getValue(cmd, ' ', 1);
      inint=instring.toInt();
      threshold = inint;
    }
    else if (cmd.startsWith("res"))
    {
      prev_read = 0;
      counter_flag = 0;
      feeding_cells = 0;
    }
  }
  if (prev_read>sensorvalue+100)
  {
    flag=1;
  }
  if (sensorvalue<threshold && flag == 1)
  {
    if(feeding_cells>=19)
    {
      counter_flag=+1;
      if(counter_flag==2)
      {
        counter_flag=0;
        stop_servo();
      }
      flag =0;
    }
    else
    {
    stop_servo();
    flag=0;
    counter_flag=0;
    }
  }
  if (pr%3000==0)
  {
    delay(2);
  }
  prev_read = sensorvalue;
}

void stop_servo()
{
  myservo.write(90);
}


void start_servo()
{
  myservo.write(90);
}

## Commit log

2021-02-01 initial sketch with working camera streams
2021-03-02 moved arduino code to repository; changed REST api to accept source ids instead of indices; added experiment flow management (untested); made changes to allow the ttl trigger to start and stop (not f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
2021-03-03 fix bug in ttl_control; reorganized config; decoupled camera id from image source id; added mqtt support; dynamically load image source classes; added video record module supporting ttl commands
2021-04-08 arena: turn touchscreen on/off; new camera configuration
2021-05-09 update flir cameras time delta when starting to write
2021-05-09 added queue to VideoWriter to fix missing frames
2021-05-12 video_record: count missed frames and largest queue size; add max size to writing queue
2021-05-16 video_record: message formatting; per image source encoding params; maximum write queue size; measure write time in queue thread
2021-06-06 arena arduino code
2021-06-06 video_record.py: report number of actually written frames
2021-06-13 feeder project files
    [Base.stl, first_cyn.stl, myGear.stl]
2021-07-02 added data logger for arena sensors
2021-07-02 remove sensor readings from the event log
2021-08-11 Prevent crash of camera process on exception when acquiring
2021-09-01 arena.py: add a check for valid sensor reading
2021-09-25 fix tasks view ui; new arena client and arduino code; cleanup
2021-09-25 feeder code encapsulated in an arduino lib
2021-10-05 arduino_arena: periodic toggling and small fixes
2021-10-05 pyspin array in camera config
2021-10-17 discrimination experiment; color flir camera and encoding; update deps; toggle multiple displays
2021-11-08 archive and delete not on main thread; fix gpu encoding parameters
2022-05-18 basic docstrings for arena/arduino code
2022-05-18 and more basic docstrings for arena/arduino code
2022-07-01 - flir_cameras: use serial instead of device if; fixes - Overlay: support multi-channel buffers\ - Save video config in json file for each recording
2022-08-04 flir_cameras: restart camera when it stops responding; fix 8bit scaling clipping; video_stream: small fix
2022-09-29 docstrings, remove log arg from task functions, fix last frame boundary in multipart video streaming
2023-01-28 video_source.py fix start frame
2023-02-20 - run arena controller as a subprocess of system - arduino ask repeatedly for configuration until received - arena: unify port and interfaces config - arena: option to upload program to a single port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
2023-02-27 ui: move socket.io handling to App component
2023-03-01 - fix getting video frame rate value - better support for webcams when using VideoImageSource
2023-03-01 print MQTT server address
2023-05-26 flir_cameras: better camera search
2023-05-26 version check and release flir camera on errors
